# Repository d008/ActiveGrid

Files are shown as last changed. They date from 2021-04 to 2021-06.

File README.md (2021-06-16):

# ActiveGrid
winglet_body.sldprt -- SolidWorks CAD files for the winglet body

winglet_lid.sldprt -- SolidWorks CAD files for the winglet lid 

winglet.brd|winglet.sch -- Eagle CAD files for the winglet PCB 

power.brd|power.sch -- Eagle CAD files for consolidating the power to each winglet at the bottom of the grid (capacity for 8 winglets each)

main.ino -- Arduino code to be uploaded onto each winglet's ESP8266

active_grid.m -- example of complementary Matlab code to drive the winglets

AG_parts_list -- list of parts and estimated budget 

Active Grid Quick Start Guide -- Instructions for running the active grid

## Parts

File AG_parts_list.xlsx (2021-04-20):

part | description | link | quantity | price | total | notes
Winglet Assembly (each) |  |  |  |  | 35.5
Winglet Body
3D-printed body & lid | files available at https://github.com/d008/ActiveGrid -- winglet.sldprt and winglet_lid.sldprt |  | 1 | 2 | 2
tube fitting | Plastic Barbed Tube Fitting for Air and Water Easy-View Adapter for 1/8" Tube x 1/8 NPT Male* |  | 1 | 1 | 1
screws | 18-8 Stainless Steel, Number 2 Size, 3/8" Long |  | 4
Winglet Electronics
custom PCB | files available at https://github.com/d008/ActiveGrid --winglet.brd/winglet.sch |  | 1 | 2 | 2
stepper motor | NW 3PCS NMB Dia 15mm 5V Deceleration Micro Motor 2 phase 4 wire Stepper Motor Step Angle 15 Degree |  | 1 | 5 | 5
stepper motor driver | BIQU A4988 Compatible StepStick Stepper Motor Diver Module with Heat Sink for 3D Printer Controller Ramps |  | 1 | 3 | 3
ESP8266 | IZOKEE Development Board for ESP8266 Compatible with Arduino |  | 1 | 4 | 4
capacitor | CAP ALUM 100UF 20% 6.3V SMD |  | 1 | 1 | 1
capsule slip ring | Senring M065-06 |  | 1 | 8 | 8 | bulk pricing available
hall effect sensor |  |  | 1 | 1 | 1
tiny magnets |  |  | 1
pin connectors & housings
Winglet frame attachments
slip ring side | Corner Bracket for Single Rail Miniature T-Slotted Framing* |  | 1 | 3.5 | 3.5
stepper-motor side | Clamping Two-Piece Shaft Collar for 1/8" Diameter, 2024 Aluminum* |  | 1 | 5 | 5
screws | Socket Head Screw M3 x 0.5 mm Thread, length as needed (~4mm) |  | 1
Active Grid Frame |  |  |  |  | 1029.44
T-slotted framing | Single Four Slot Rail, Silver, 20 mm Square, Solid, 2 ft (one of which is cut into four 6" sections) |  | 5 | 8.28 | 41.4
 | Single Four Slot Rail, Silver, 20 mm Square, Solid, 4 ft |  | 4 | 13.93 | 55.72
 | Gusset Bracket for 20mm High Rail, 1-5/8" Long, Silver |  | 4 | 9.24 | 36.96
 | Silver Open Gusset Bracket for 20mm High Rail, 3/4" Long |  | 4 | 5.04 | 20.16
 | Silver 90 Degree Surface Bracket for 20 mm High Rail |  | 4 | 10.99 | 43.96
 | Black Plastic Pull Handle for 20 mm High Rail, 5-3/16" Long |  | 2 | 8.34 | 16.68
Miniature T-slotted framing | Single Rail, 10 mm High x 10 mm Wide, 24" |  | 8 | 9.93 | 79.44
 | Single Rail, 10 mm High x 10 mm Wide, 12" |  | 20 | 4.95 | 99
 | Single Rail, 10 mm High x 10 mm Wide, 6" |  | 44 | 2.47 | 108.68
 | Corner Bracket for Single Rail Miniature T-Slotted Framing |  | 128 | 3.5 | 448
 | Corner Surface Bracket for Single Rail Miniature T-Slotted Framing |  | 8 | 4.68 | 37.44
 | Truss Surface Bracket for Single Rail Miniature T-Slotted Framing |  | 8 | 5.25 | 42
Power Supplies |  |  |  |  | 280
custom PCB | files available at https://github.com/d008/ActiveGrid -- power.brd/power.sch |  | 8 | 1 | 8
5V power supply | 5v 7A Dc Universal Switching Power Supply |  | 8 | 13 | 104
12V power supply | 12v 30a Dc Universal Regulated Switching Power Supply 360w |  | 8 | 21 | 168
pin connectors & housings
screw terminals
 |  |  | total (60 winglets) |  | 3439.44
* requires modifications (see image below)

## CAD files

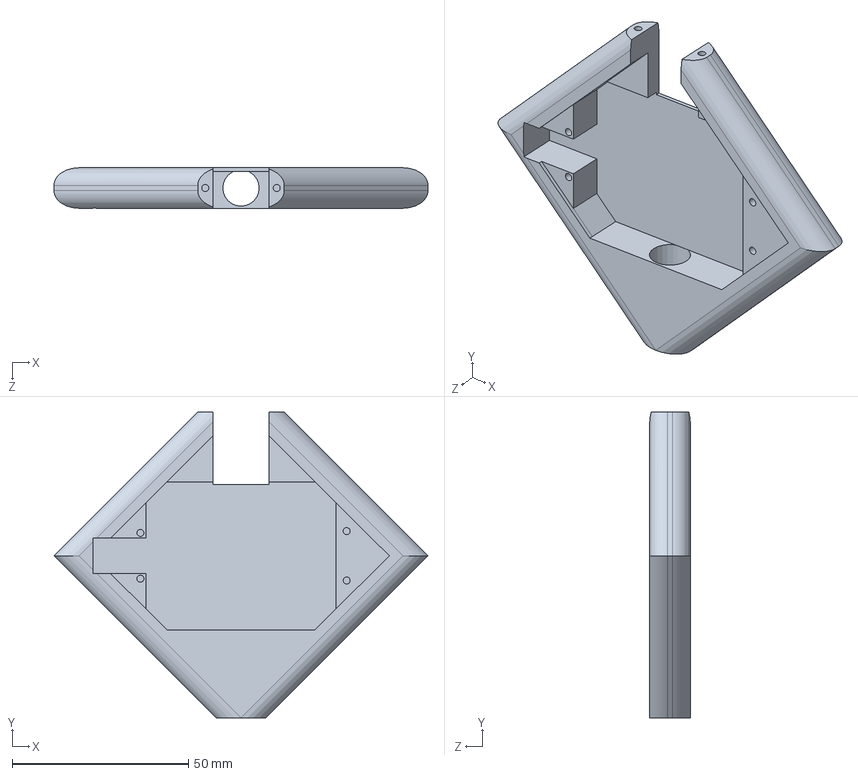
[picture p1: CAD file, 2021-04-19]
winglet_body.sldprt
106.1 x 86.8 x 11.5 mm

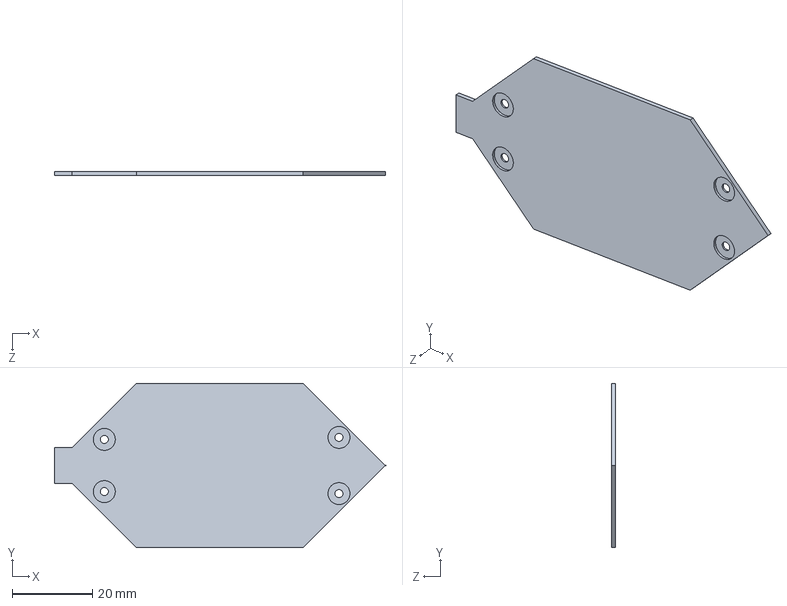
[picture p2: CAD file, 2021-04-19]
winglet_lid.sldprt
82.5 x 41.0 x 1.00 mm

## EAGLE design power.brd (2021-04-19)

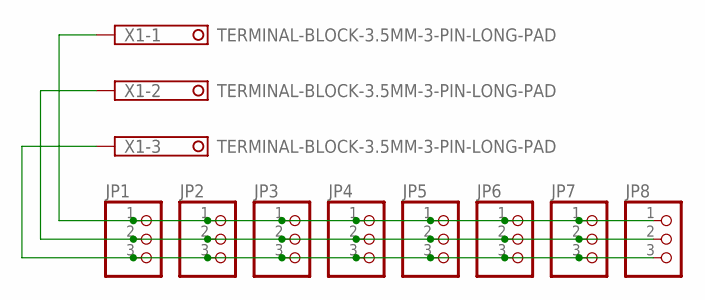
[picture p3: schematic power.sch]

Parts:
JP1, JP2, JP3, JP4, JP5, JP6, JP7, JP8: PINHD-1X3/90; 1X03/90
X1: TERMINAL-BLOCK-3.5MM-3-PIN-LONG-PAD; TERMINAL-BLOCK-3-PIN-3.5MM-LONG-PAD

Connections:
unnamed: JP1.1, JP2.1, JP3.1, JP4.1, JP5.1, JP6.1, JP7.1, JP8.1, X1.1
unnamed: JP1.2, JP2.2, JP3.2, JP4.2, JP5.2, JP6.2, JP7.2, JP8.2, X1.2
unnamed: JP1.3, JP2.3, JP3.3, JP4.3, JP5.3, JP6.3, JP7.3, JP8.3, X1.3

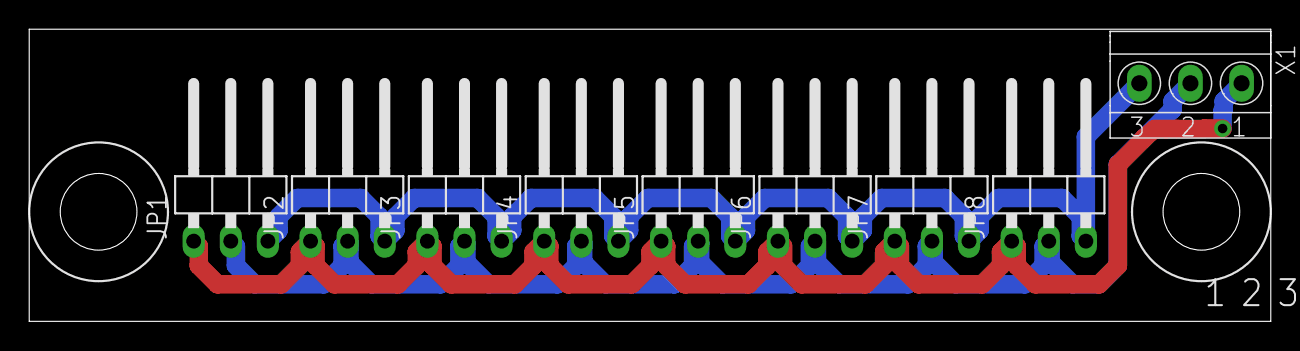
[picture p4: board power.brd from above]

Board: 2 copper layers, 85.0 x 20.0 mm, 9 parts (0 on the bottom side), 3 nets.

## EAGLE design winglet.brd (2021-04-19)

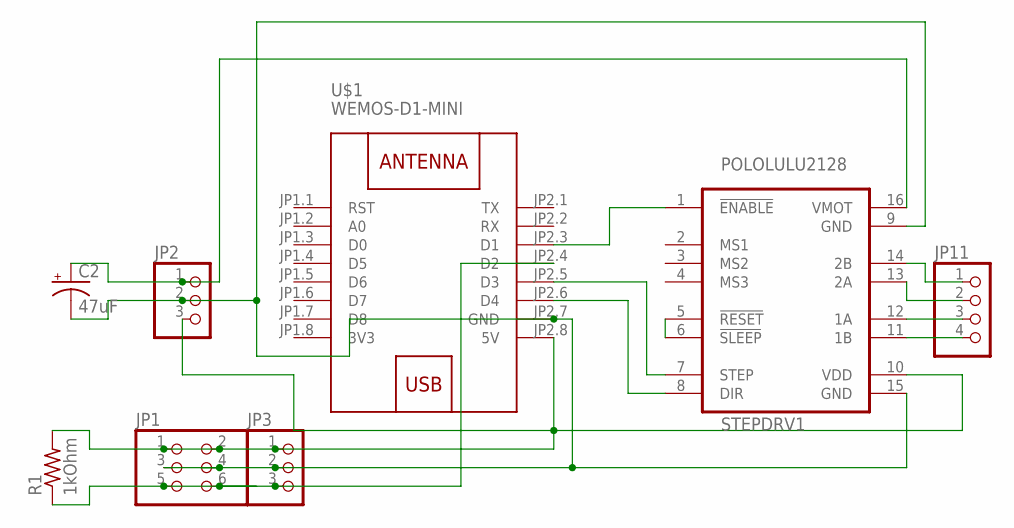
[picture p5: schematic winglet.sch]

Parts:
C2: 47uF; PANASONIC_D
JP1: PINHD-2X3; 2X03
JP2: PINHD-1X3/90; 1X03/90
JP3: PINHD-1X3; 1X03
JP11: PINHD-1X4/90; 1X04/90
R1: 1kOhm; M1206
STEPDRV1: POLOLULU2128
U$1: WEMOS-D1-MINI

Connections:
3V3: U$1.JP1.8 (3V3)
unnamed: JP1.1, JP1.2, JP2.3, JP3.1, R1.2, STEPDRV1.10 (VDD), U$1.JP2.8 (5V)
unnamed: C2.-, JP1.3, JP1.4, JP2.2, JP3.2, STEPDRV1.9 (GND), STEPDRV1.15 (GND), U$1.JP2.7 (GND)
unnamed: JP1.5, JP1.6, JP3.3, R1.1, U$1.JP2.4 (D2)
unnamed: STEPDRV1.5 (!RESET), STEPDRV1.6 (!SLEEP)
unnamed: STEPDRV1.1 (!ENABLE), U$1.JP2.3 (D1)
unnamed: STEPDRV1.7 (STEP), U$1.JP2.5 (D3)
unnamed: C2.+, JP2.1, STEPDRV1.16 (VMOT)
unnamed: STEPDRV1.8 (DIR), U$1.JP2.6 (D4)
unnamed: JP11.4, STEPDRV1.11 (1B)
unnamed: JP11.3, STEPDRV1.12 (1A)
unnamed: JP11.2, STEPDRV1.13 (2A)
unnamed: JP11.1, STEPDRV1.14 (2B)

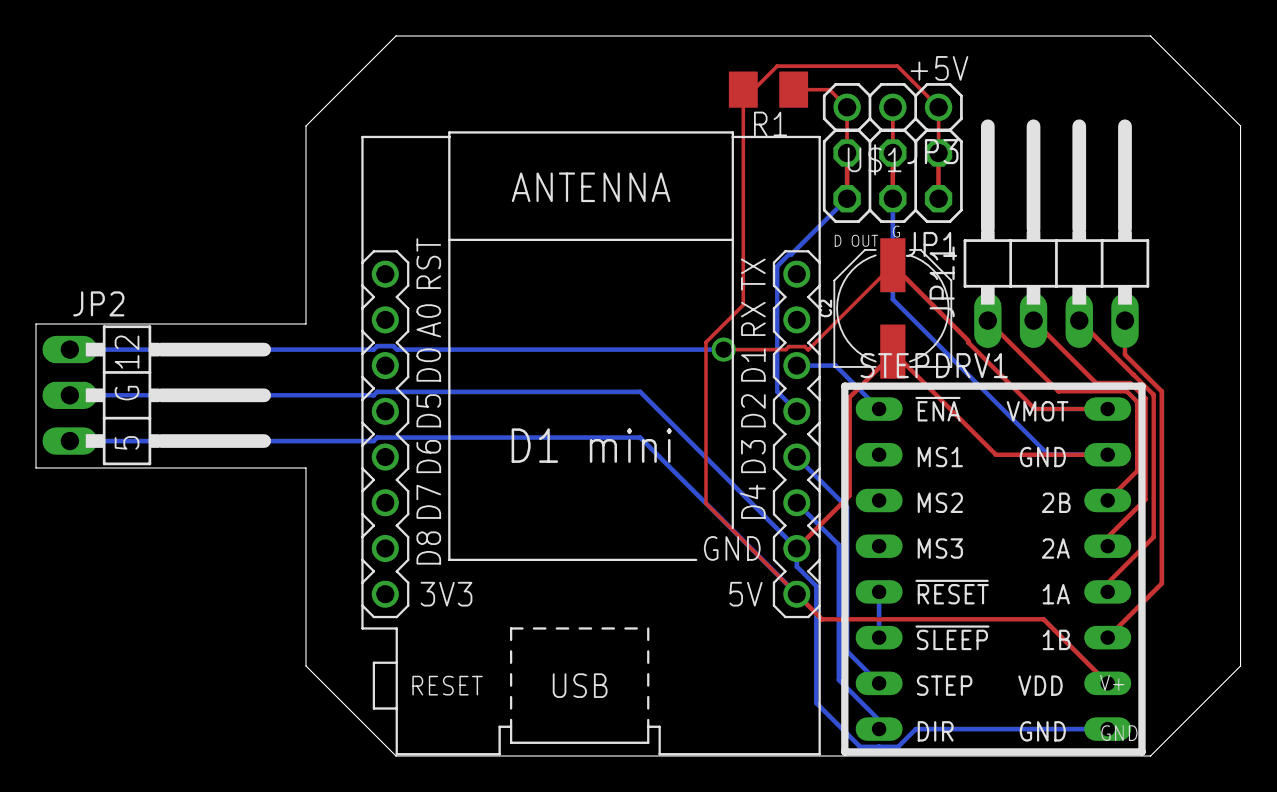
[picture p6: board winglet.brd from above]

Board: 2 copper layers, 66.9 x 40.0 mm, 8 parts (0 on the bottom side), 12 nets.

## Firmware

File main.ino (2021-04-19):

// sudo chmod a+rw /dev/ttyUSB0
// :D 

#include <ESP8266WiFi.h>
#define dirPin 2
#define stepPin 0
#define stepsPerRevolution 1000
#define hallPin 4
#define enablePin 5

const char* ssid     = "TP-LINK_6BCD"; // name of the wireless network
const char* password = "51360306"; // password of the wireless network
String dirString = "0";
String delayString = "2000";
String stepdegString = "1";
String timesString = "1"; 
int dir = 0;
int delayMS = 500;
int stepDeg = 1;
int steps = 5; 
int times = 1; 

WiFiClient client;
WiFiServer server(80);  // Set web server port number to 80

// NETWORK: Static IP details
IPAddress ip(192,168,0,183);  // this will be unique to each winglet
IPAddress gateway(192,168,0,0);
IPAddress subnet(255,255,255,0);


void setup() {
  // Sets the two pins as outputs
  pinMode(stepPin,OUTPUT); 
  pinMode(dirPin,OUTPUT);
  pinMode(hallPin, INPUT);
  pinMode(enablePin, OUTPUT);

  digitalWrite(enablePin,HIGH); // high disables
  
  Serial.begin(115200);
  delay(10);

  // Connect WiFi
  Serial.println();
  Serial.println();
  Serial.print("Connecting to ");
  Serial.println(ssid);

  // Static IP setup info 
  WiFi.config(ip,gateway,subnet);

  // Start server
  WiFi.hostname("Name");
  WiFi.begin(ssid, password);
  
  
  while (WiFi.status() != WL_CONNECTED) {
    delay(500);
    Serial.print(".");
  }
  Serial.println("");
  Serial.println("WiFi connected");
 
  // Print the IP address
  Serial.print("IP address: ");
  Serial.println(WiFi.localIP());
  
  server.begin();
}





void loop() {
  // Check if a client has connected
  WiFiClient client = server.available();
  client.setNoDelay(1);
  if(client)
    {
      Serial.println("New Client");
      String req = ""; 
      while (client.connected())
        {
          while(client.available())
            {
              
              Serial.println("client available");
              String req = client.readStringUntil('\r');
              Serial.println(req);


              if (req.indexOf("X") != -1) 
                {
                  digitalWrite(enablePin,LOW);
                  
                }

        
              if (req.indexOf("H") != -1) 
                {
                  digitalWrite(enablePin,LOW);
                  digitalWrite(dirPin,HIGH);
                  while(digitalRead(hallPin))
                    {
                      digitalWrite(stepPin,HIGH);
                      delayMicroseconds(1000);
                      digitalWrite(stepPin,LOW);
                      delayMicroseconds(1000);
                      yield();
                    }
                   digitalWrite(enablePin,HIGH);
                   digitalWrite(enablePin,HIGH);
                }
                

                if (req.indexOf("R") != -1)
                  {
                    digitalWrite(enablePin,LOW);
                    dirString = req[req.indexOf("R")+1];
                    delayString = req.substring(req.indexOf("D")+1,req.indexOf("S"));
                    stepdegString = req.substring(req.indexOf("S")+1,req.indexOf("T"));
                    timesString = req.substring(req.indexOf("T")+1);
                    long dir = dirString.toInt();
                    long delayMS = delayString.toInt();
                    long stepDeg = stepdegString.toInt();
                    steps = stepsPerRevolution*stepDeg/360L;
                    int times = timesString.toInt();
                    Serial.println(dir); 
                    Serial.println(delayMS); 
                    Serial.println(stepDeg); 
                    Serial.println(times); 
                    
                    digitalWrite(dirPin,dir);
                    for (int j = 1; j<times+1; j++){
                      for (int i = 0; i < steps; i++) {
                        // These four lines result in 1 step:
                        digitalWrite(stepPin, HIGH);
                        delayMicroseconds(delayMS);
                        digitalWrite(stepPin, LOW);
                        delayMicroseconds(delayMS);
                        yield();
                      }
                    }
                    digitalWrite(enablePin,HIGH);
                  }

//                if (req.indexOf("S") != -1)
//                  {
//                    digitalWrite(enablePin,LOW);
//                    dirString = req[req.indexOf("S")+1];
//                    stepdegString = req.substring(req.indexOf("S")+2);
//                    long dir = dirString.toInt();
//                    long stepDeg = stepdegString.toInt();
//                    digitalWrite(dirPin,dir);
//                    steps = stepsPerRevolution*stepDeg/360L;
//                    Serial.println(steps);
//                    
//                    for (int i = 0; i < steps; i++) {
//                      // These four lines result in 1 step:
//                      digitalWrite(stepPin, HIGH);
//                      delayMicroseconds(1000);
//                      digitalWrite(stepPin, LOW);
//                      delayMicroseconds(1000);
//                      yield();
//                    }
//                    digitalWrite(enablePin,HIGH);
//                  }
                
              client.flush();
              break;
              
            }
        }
      client.stop();
      Serial.println("Client disconnected.");
      Serial.println("");  
    }
  
  
}

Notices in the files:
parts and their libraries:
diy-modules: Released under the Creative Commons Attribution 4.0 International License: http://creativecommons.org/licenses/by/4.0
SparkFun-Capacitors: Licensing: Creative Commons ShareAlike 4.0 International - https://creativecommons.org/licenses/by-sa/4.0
